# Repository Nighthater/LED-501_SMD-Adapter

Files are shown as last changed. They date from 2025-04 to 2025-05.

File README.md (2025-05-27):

# LED-501 SMD Adapter
Adapter Mount for the LED-501 mount from Instrument Systems  

Fit any SMD LED or other Parts onto this mount

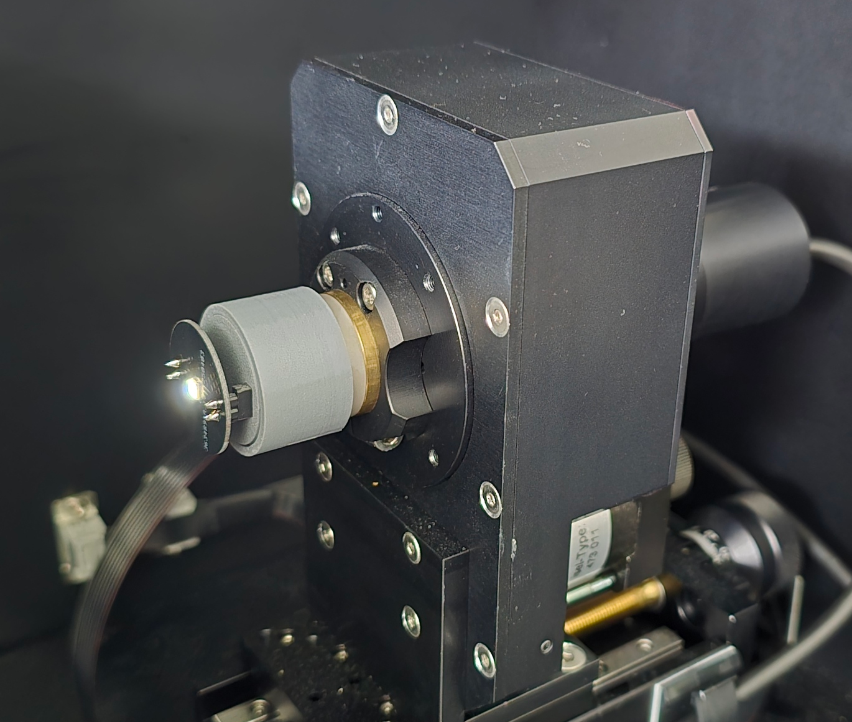
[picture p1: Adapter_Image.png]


## Parts Needed:
- 3D Printer (To Manufacture the Adapter and Assembly Tools, any 3D Print service does the job)
- 2x Standard 2.54mm Female 01x02 Pin Headers 
- 2x Standard 2.54mm Male 01x02 Pin Headers
- PCBs
- SMD LEDs
- 5mm THT LED (Serves as adapter for the LED-501 mount)
- Flat Side cutter (Knipex 78 61 125 or similar)
- Superglue
- Soldering Iron for Headers
- Hot Air Station for SMD LEDs

## Custom PCBs
If you want to test other SMD LEDs than the included 2835 footprint, you can create your own LED Board.
Doing this is simple and can be done in any EDA Software within minutes.

#### Specifications
- The PCB Outline is a 25mm Circle.
- The LED is placed in the exact centre of the circle.
- The Header pins are placed +/- 8.5mm from the Centre.
- Make sure the GND and VCC contacts are each on the same side as the Base PCB. (e.g. GND Both Left, VCC Both Right) You can swap polarities by roating the PCB.

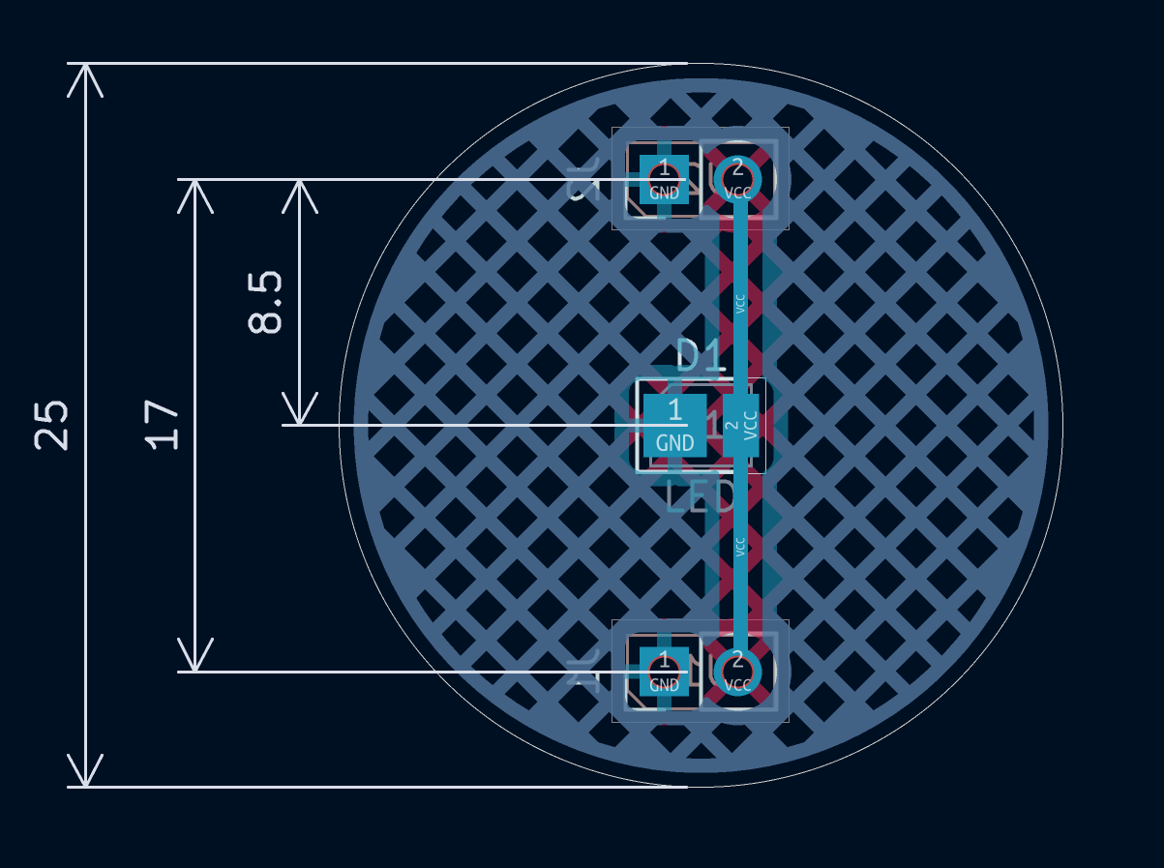
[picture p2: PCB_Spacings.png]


## Assembly

#### Printing Instructions

All parts, except the Adapter (010) can be printed directly without supports.
Be sure to enable rectangular supports for the Adapter.

If you cannot get a somewhat even surface for the PCB to sit on after removing the supports, try angling the adapter 45°, print at a low layerheight (< 0.12 mm) and use a raft and supports (Increase the threshold angle!) for adhesion.

#### Bottom PCB

- Take The Round Assembly Tool Spacer (100) and place the PCB into the Marked Section onto the Assembly Tool.
- Use the PCB Holder (110) to fix the PCB in place
- Insert the 5mm LED and fix it in place using the LED Holder Guide (120), then place and fix the LED with the holder (130)
- Solder the LED in place
- Remove the Assembly Tools
- Use a flat side cutter (Knipex 78 61 125 or similar) to cut off the top LED portion   
- Place the PCB into the Heaxagonal Tool (200)
- Insert the Female 2.54mm 1x2 headers 
- The Headers should face in the opposite direction from the Leads (The LED Leads go upwards, the Headers downwards)
- Place the Assembly upside down onto a flat surface, the headers are now aligned
- Solder the Headers onto the PCB
- Glue the PCB into the Adapter Part (010)   
- Glue the Front cover (020) onto the Adapter
- To protect the LED Leads from damage, you can use the Contact Cover (030)

#### Top PCB

- Solder your SMD LED onto the Top PCB
- Insert the Male 2.54mm 1x2 headers facing away from the SMD LED
- Put the PCB with the headers into the Base PCB, ensuring that the contacts are aligned
- Solder the Headers

The Adapter is now finished and ready for use

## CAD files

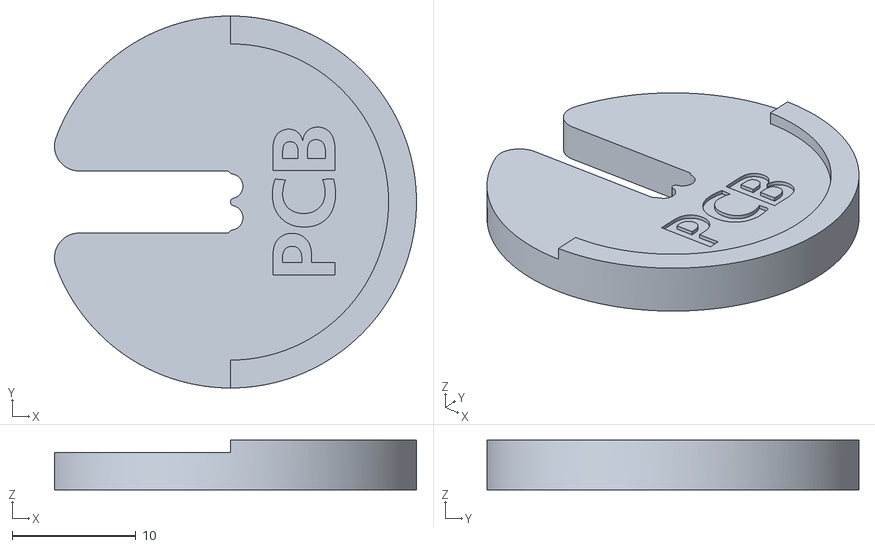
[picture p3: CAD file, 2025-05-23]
100_Assembly_Tool_Spacer.stl
29.2 x 30.0 x 4.00

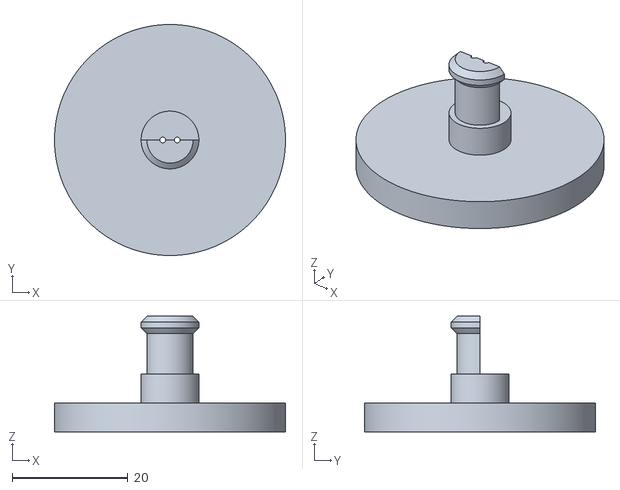
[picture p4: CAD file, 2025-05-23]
140_Assembly_Tool_Wires.stl
40.0 x 40.0 x 20.0

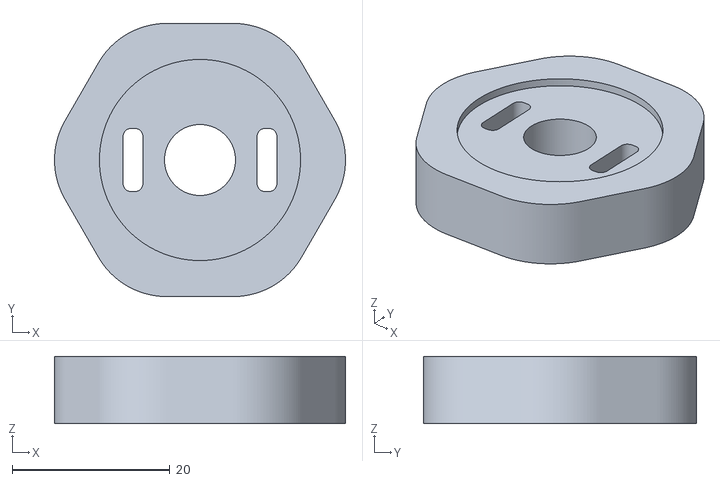
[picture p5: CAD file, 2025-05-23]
200_Assembly_Tool_Headers.stl
36.9 x 34.6 x 8.50

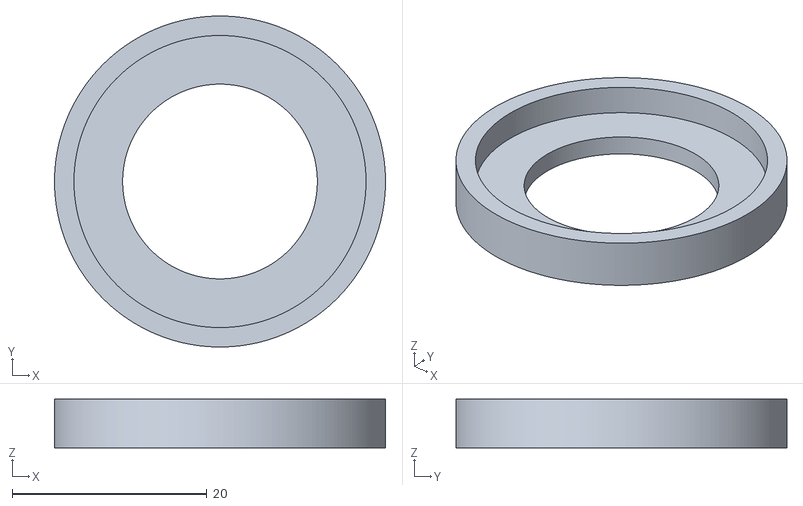
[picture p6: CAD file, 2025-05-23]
110_Assembly_Tool_PCB_Holder.stl
34.0 x 34.0 x 5.00

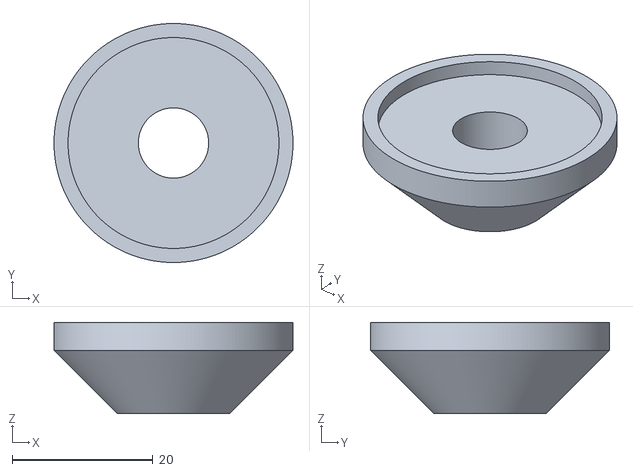
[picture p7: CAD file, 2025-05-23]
120_Assembly_Tool_LED_Holder_Guide.stl
34.0 x 34.0 x 13.0

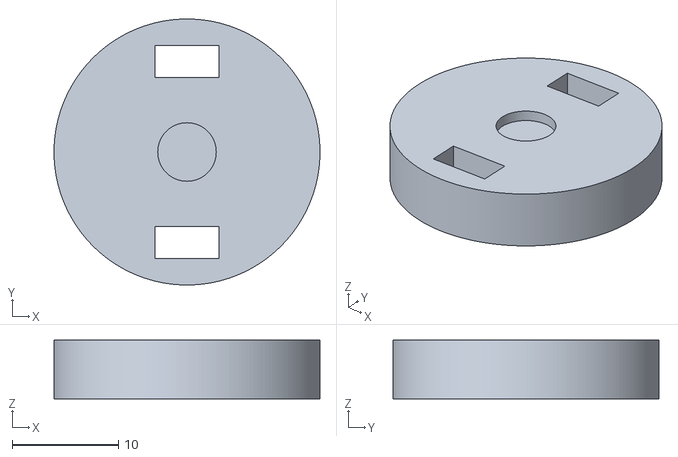
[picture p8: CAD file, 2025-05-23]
020_Adapter_Front_Cover.stl
25.0 x 25.0 x 5.50

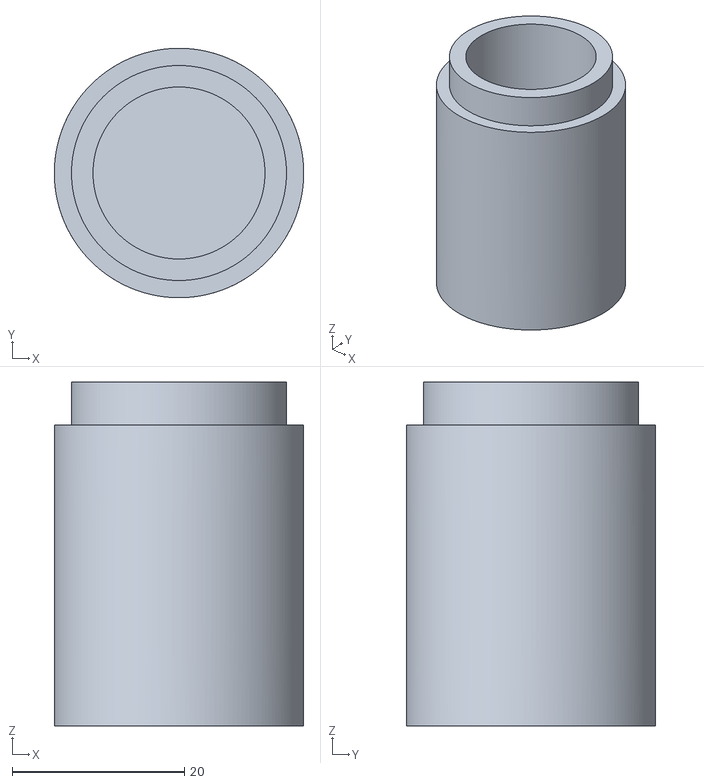
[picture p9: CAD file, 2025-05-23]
030_Adapter_Contact_Cover.stl
29.0 x 29.0 x 40.0

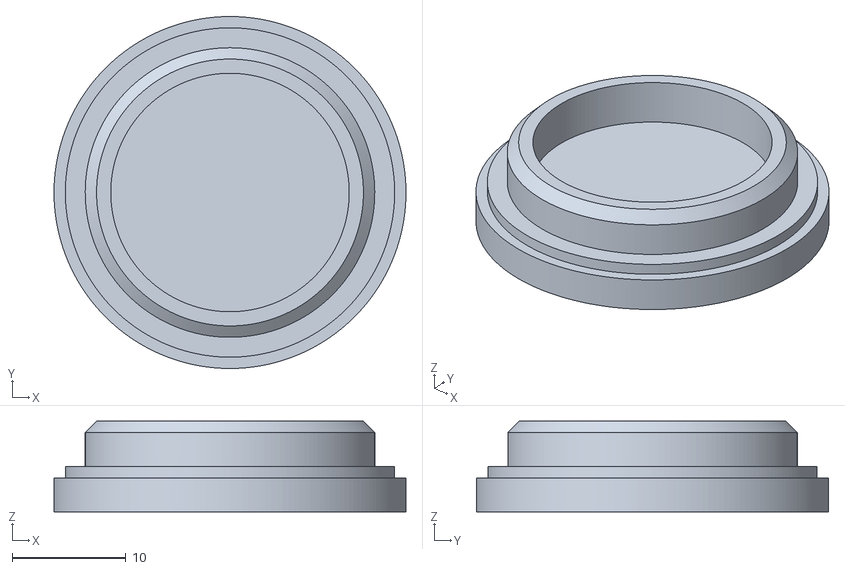
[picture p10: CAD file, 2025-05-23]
410_LED_PCB_Lid.stl
31.0 x 31.0 x 8.00

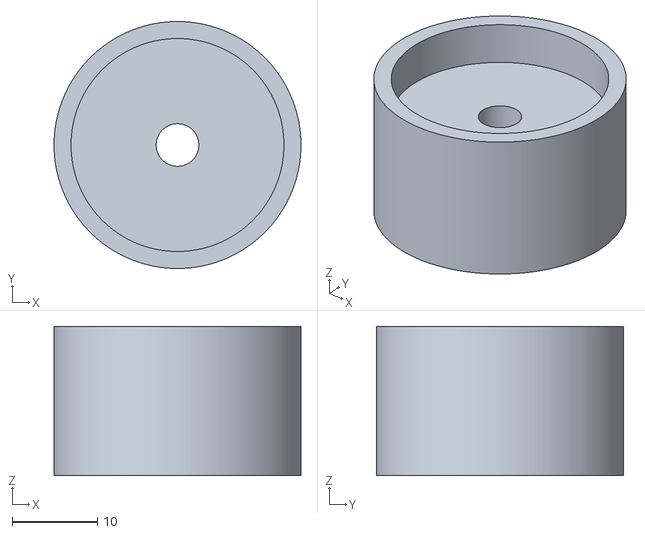
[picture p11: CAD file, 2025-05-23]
010_Adapter.stl
29.0 x 29.0 x 17.5

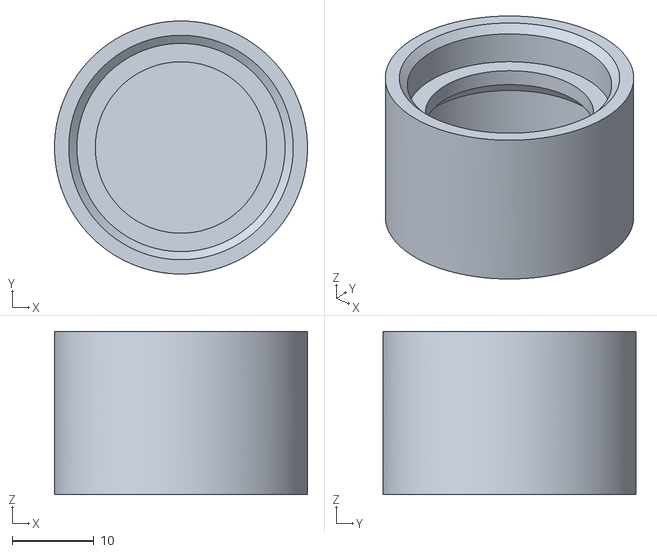
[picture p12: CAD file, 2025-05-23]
400_LED_PCB_Case.stl
31.0 x 31.0 x 20.0

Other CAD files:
130_Assembly_Tool_LED_Holder.stl

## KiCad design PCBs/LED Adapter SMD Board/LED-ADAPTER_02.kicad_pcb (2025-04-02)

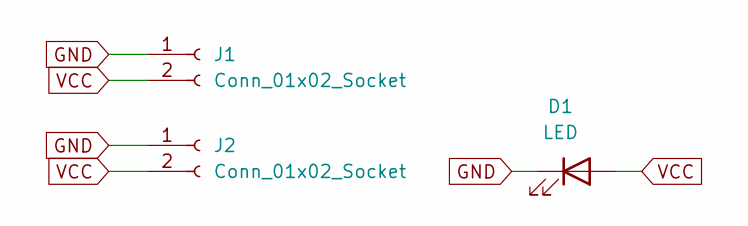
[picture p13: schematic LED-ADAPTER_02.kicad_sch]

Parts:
D1: LED; LED_PLCC_2835
J1, J2: Conn_01x02_Socket; PinSocket_1x02_P2.54mm_Vertical

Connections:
GND: D1.1 (K), J1.1, J2.1
VCC: D1.2 (A), J1.2, J2.2

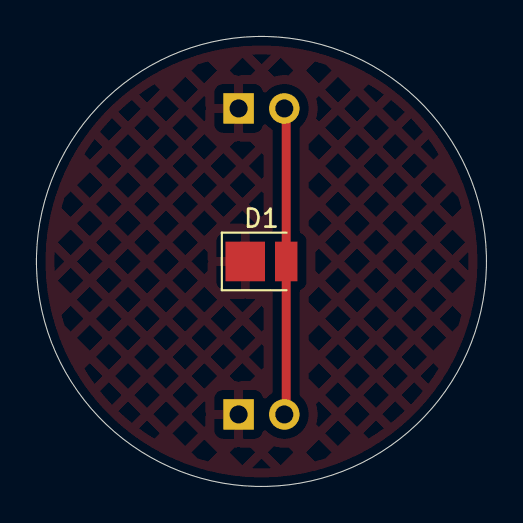
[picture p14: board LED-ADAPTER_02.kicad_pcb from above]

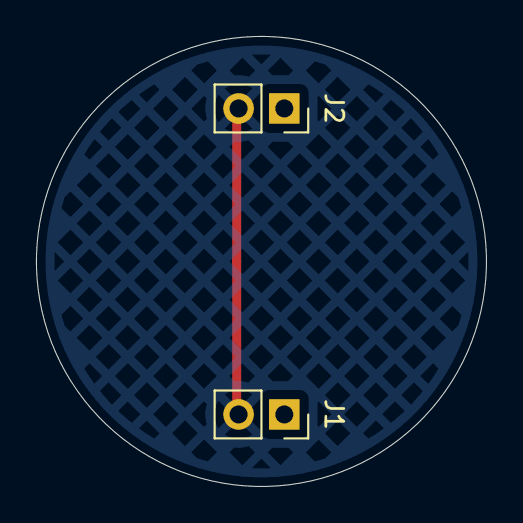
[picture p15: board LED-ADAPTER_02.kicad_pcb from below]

Board: 2 copper layers, 25.0 x 25.0 mm, 3 parts (2 on the bottom side), 2 nets.

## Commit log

2025-04-02 Added PCBs
    [LED-ADAPTER_01.kicad_pcb, LED-ADAPTER_01.kicad_sch, LED-ADAPTER_02.kicad_pcb, LED-ADAPTER_02.kicad_sch]
2025-04-02 Add 3D Printed Adapter
    [Adapter.stl]
2025-04-17 Added Assembly Tools
    [Assembly_Tool_5mm_LED.stl, Assembly_Tool_Headers.stl]
2025-04-17 Refitted Adapter
    [Adapter.stl]
2025-05-05 3D Printed Parts
    [100_Assembly_Tool_Spacer.stl, 10_Adapter.stl, 110_Assembly_Tool_PCB_Holder.stl, 120_Assembly_Tool_LED_Holder_Guide.stl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]
2025-05-23 Added PCB Image
2025-05-23 Fixed Orientations
    [100_Assembly_Tool_Spacer.stl, 10_Adapter.stl, 110_Assembly_Tool_PCB_Holder.stl, 120_Assembly_Tool_LED_Holder_Guide.stl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]
2025-05-23 Renamed Files
    [010_Adapter.stl, 020_Adapter_Front_Cover.stl, 030_Adapter_Contact_Cover.stl]
